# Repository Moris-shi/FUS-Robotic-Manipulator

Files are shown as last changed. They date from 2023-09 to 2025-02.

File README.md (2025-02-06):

# FUS-Robotic-Manipulator

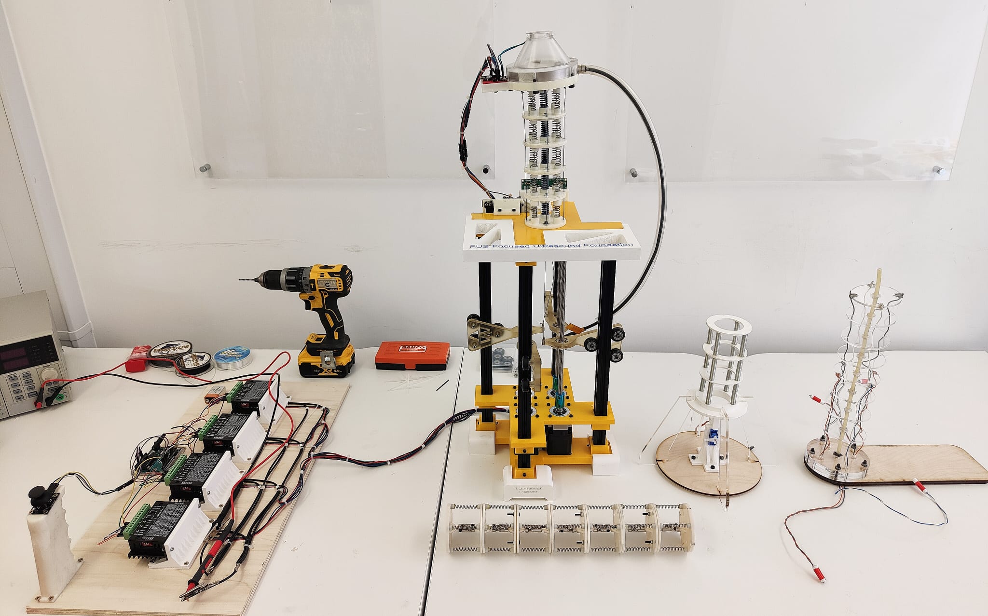
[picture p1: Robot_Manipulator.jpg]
image alt

 
Please refer to the project abstract and FUS report first which contains all information on development of the manipulator and assembly instructions

The robot CAD files section contains all the components in .stl format. This was 3D printed on a Ultimaker 2+ connect printer but any other 3D printer with a sufficent build volumn could be used. For 3D printing, import the .stl files into Ultimaker Cura available at https://ultimaker.com/software/ultimaker-cura/.
The following quantities of each file is needed:

•	1 x Base Mount

•	1 x Stepper Motor Mount

•	1 x Top Mount

•	4 x Slider

•	4 x Base Support Legs

•	1 x Sideways Support Mount

•	4 x Stepper Motor TB6600 Controller Mount

•	1 x LCD Mount

•	1 x Arduino Mount

•	1 x Joystick Mount

•	10 x Tendon Ligaments

•	1 x Ultrasonic Transducer Mount

The hardware section contains an Excel spreadsheet with all the hardware which needs to be purchased including prices (UK) and non-sponsored, sourcing links.

Robot Code section contains the required Arduino codes for the project

Any questions please contact me at zcemxsh@ucl.ac.uk

I would also love to hear if any replications or improvements have been made

Thank you for taking the time to check out this project

# Acknowledgement
We acknowledge the Focused Ultrasound Foundation for providing funding and supporting this project through the 2023 Global Internship Program.

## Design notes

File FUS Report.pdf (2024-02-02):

## Developing an affordable open-source robotic platform for precisely manipulating ultrasonic transducers for laboratory experimental FUS studies

Xingzao Shi, Student Member, University College London and Dr Seyyed Reza Haqshenas, Lecturer Of Therapeutic Ultrasonics, University College London

DECLARATION

“I, Xingzao Shi, confirm that the work presented in this report was my own. Where information has been derived from other sources, I confirm that this has been indicated in the report.”

## Abstract

This report will provide in-depth documentation on the development of a robotic platform designed to manipulate focused ultrasound (FUS) transducer for therapeutic applications. It will begin with an introduction to FUS technology, highlighting the challenges associated with its manipulation in laboratory settings.

Subsequently, design specifications aimed at addressing these challenges will be outlined. A comprehensive background research and literature review follows, with a focus on selecting the optimal robotic mechanism for the manipulator.

Moving forward, the development process of the robot was documented, including the various prototypes and designs, as well as the integration of electronics and sensors. Additionally, assembly blueprints and step-by-step instructions for building the robot from scratch will be provided. Testing will be conducted at each stage of development, with detailed documentation of the results obtained.

Finally, the report will conclude by discussing potential avenues for future improvements and provide a comprehensive list of references for further reading.

## Acknowledgement

I would like to extend special thanks to the Focused Ultrasound Foundation (FUS) who generously funded this project as part of the Charles Steger ACCESS FUS internship. Their support has been indispensable in bringing this project to life.

I would also like to thank all the researchers whose findings have been invaluable in the development of the robot as well as UCL Mechanical Engineering for providing the facilities and workshop.

Finally, I also want to express my deep appreciation to Dr Reza Haqshenas for his unwavering support and mentorship throughout the project.

## Table of Contents

## List of Figures

## List of Tables

Table 1: | 20
Table 2: | 25
Table 3: | 38
Table 4: | 38
Table 5: | 43
Table 6: | 66
Table 7: | 68

## A) Background

## I – Introduction

Focused Ultrasound (FUS) is an emerging medical technology that uses ultrasound waves to treat various medical conditions. FUS works on the principle of focusing ultrasound waves onto a specific target area in the body. This was done by using multiple ultrasonic transducers and firing them so that all the individual waves focus on one point through interference and superposition. At the focal point, the high energy frequencies can cause thermal ablation and heating destroying the cells in the local area or it can trigger cavitation, imploding the target zone. [1] The focused nature means that the effect was only localized at the focal region without affecting surrounding healthy tissue. FUS was usually implemented with MRI guidance to locate and assess the treatment at the target location. Currently, it is used as a non-invasive or minimally invasive technique for therapeutic purposes in different medical fields, including oncology, urology, and neurology.

- Oncology: FUS was commonly used in the treatment of various types of cancer, including prostate cancer and uterine fibroids. In prostate cancer treatment, FUS can be used to precisely target and thermally ablate cancerous tissue within the prostate gland while minimizing damage to nearby structures. It was considered a less invasive alternative to surgery or radiation therapy.
- Urology: FUS can also be used in urology to treat conditions like kidney stones. The high intensity of the focused ultrasound creates shockwaves and shatters the kidney stones.
- Neurology: Neurological disorders such as Parkinson’s and essential tremors can be treated with FUS where the region of the patient’s brain responsible for the condition can be targeted.
- Drug delivery: The challenge of precise drug delivery can be solved by FUS. The drug was injected intravenously into the patient in temperature-sensitive gel carriers. Then, FUS can be used to raise the temperature of the target location melting the carriers and releasing the drug at the target location.

Benefits of FUS include reduced risk of infection, minimal scarring, shorter recovery times, and potentially fewer side effects compared to traditional surgical procedures. However, the effectiveness of FUS can vary depending on the specific condition being treated, the size and location of the target tissue, and individual patient factors.

## B) Motivation

In therapeutic ultrasound, ultrasonic energy was focused on the target tissue to induce bioeffects. To treat the entire volume, the ultrasonic beam was steered either electronically, mechanically, or electromechanically (in hybrid equipment). Electrical steering utilises an array of multiple transducers firing out of phase to direct and move the focal point of the ultrasounds through interference. This was a very versatile but expensive option. On the other hand, mechanical steering can be carried out by utilising a robotic platform whereby the transducer was attached to a robot and the focal point moved by controlling the robot.

However, current robot platforms for ultrasonic transducer manipulation are heavily commercialised and very expensive. Often, complex proprietary software was used to control them, and it was very difficult to modify the design for bespoke applications. Solutions such as the MGIUS-R3 cost upwards of 100,000 pounds [2] and although being very capable, the price makes it out of reach for most researchers. This was a problem, and a cost-effective DIY robotic platform needs to be developed to allow more researchers to be able to precisely control the position and orientation of ultrasound transducers. The project will be open-sourced to allow other researchers to access the required designs for 3D printing and add improvements to the design.

The robot needs to be affordable yet reliable and capable. It must also be possible for a fellow researcher with basic mechatronics knowledge and experience to fabricate. The following design specifications are based on the general requirements of researchers in focused ultrasound.

- Cost – The cost of the robot was to be kept under five hundred pounds for all materials and parts.
- Simplicity of design and construction – All components should be easily sourced online, and all custom parts should be 3D printed with .stl files available for download. The assembly should be clear and easy to follow using nuts and bolts rather than welds or wood joining work.
- Load carrying capabilities – The robot should be able to successfully manipulate an ultrasonic transducer weighing up to five hundred grams.
- Workspace – The robot should have a field of reach of around 300mm from the base to the tip of the ultrasonic transducer.
- Ease of use – The robot needs to have an intuitive and simple form of control with a user-friendly display interface. The codes for this should be open-sourced for further development and improvements.
- Precision – The precision of the robot should be in the tolerance of millimetres in terms of positioning and sensing.
- Durability – The robot needs to be durable for repeated operation within its intended use.

## II – Manipulator Selection

## A) Robot Mechanisms

From the motivation and parameters, a design for a robotic manipulator for the ultrasonic transducer was required. Initially, to start the designing process, a class of manipulator mechanisms needs to be selected. For this purpose, thorough research into different types of manipulators was conducted.

### 1) Serial Manipulators

A serial robot consisting of a series of interconnected links joined by moving joints in a sequential chain-like structure. [3] Each joint can either be prismatic adding a linear motion variable, or revolute adding a new rotational axis and degree of freedom. Either allows motion between their adjacent links, enabling the robot to manipulate objects in its workspace. Serial robots have a rigid base and an end-effector, which is the part of the robot that interacts with the environment or performs specific tasks. In this case, the end effector would be the ultrasonic transducer.

Figure 1: Serial robot manipulator [4]

An example of a serial robot is an articulated robot commonly seen in industrial applications such as vehicle assembly lines. These robots often have multiple revolute joints and thus multiple degrees of freedom allowing them to achieve a wide range of motions such as reaching, picking, placing, and manipulating objects within their workspace.

Serial robots excel in precision, accuracy, and repeatability in performing tasks. They can be programmed to follow specific trajectories and manipulate objects with high dexterity. However, due to their sequential structure, they may have limitations in terms of speed and payload capacity as high moments and torques occur around the joints.

To achieve motion, an articulated robot can include either revolute, linear or spherical joints.

- A revolute joint moves around an axis achieving rotational motion. It provides a single degree of freedom, allowing rotation along one axis while constraining motion along the other axes.
- A linear or prismatic joint can move in a translational motion along a single axis this can be in the form of a sliding mechanism or piston actuating the joint making it longer or shorter.

- A spherical joint can move in multiple degrees of freedom around a single point. It was the combination of three revolute joints with an axis that intersects at a common point.

### 2) Parallel Manipulators

Figure 2: Mechanism types [5]

A parallel robot utilises multiple independent kinematic chains and links to connect the base of the robot to the end effector. [6] Each kinematic chain was independently actuated, allowing the robot to move the end effector in a coordinated manner. The design of a parallel robot allows for simultaneous control of multiple degrees of freedom from a single joint. An example of a parallel manipulator was a delta robot with three kinematic chains. This design provides excellent speed, accuracy, and agility, making delta robots well-suited for tasks that require rapid and precise positioning such as pick and place operations.

Figure 3: Parallel manipulator [7]

One characteristic feature of parallel robots is that they distribute the forces and loads among multiple limbs, allowing for better stability and load-carrying capacity. This attribute makes them suitable for applications that require high stiffness and heavy payload handling, such as flight simulators, machining, and heavy-duty industrial tasks. Parallel robots are also known for their exceptional accuracy, as their design reduces the effects of individual joint and link tolerances, resulting in precise and repeatable motion. They are often used in applications that demand high accuracy, such as surgical robots and 3D printing.

However, parallel robots can be more complex to design, and control compared to serial robots due to the interdependencies between the limbs and the need for coordinated motion. In addition, their workspace was also more limited compared to serial robots, as the range of motion was constrained by the mechanical structure. Furthermore, parallel manipulators are very sensitive to small errors in control signals or component defects as a small error was magnified by the mechanism having a large knock-on effect on the position of the end effector.

### 3) Hybrid Manipulators

A hybrid manipulator incorporates elements of both serial and parallel robots to combine their features and leverage their respective advantages and overcome limitations. [8] For example, a hybrid robot might use a serial robot arm for precise manipulation tasks and incorporate a parallel mechanism for increased stiffness and load-carrying capacity. This helps to improve their versatility, adaptability, and efficiency in performing complex tasks.

Figure 4: Hybrid manipulator [9]

An example of a hybrid manipulator was a serial-parallel robot. This type of hybrid robot has a serial robotic arm for reaching long distances and performing complex tasks, along with a parallel mechanism before the end effector for increased stability, load-carrying capacity, or high-speed operations. The combination of serial and parallel components allows for improved performance in terms of precision, speed, and versatility.

However, hybrid manipulators are the most complex to design, code and manufacture. And their nature of combining serial and parallel components makes them the most expensive option. Furthermore, hybrid mechanisms have increased failure points which make them less reliable and require more maintenance.

### 4) Cartesian Manipulators

Cartesian manipulators are very simple in design and can have a very large workspace. As a result, they are primarily used for transferring heavy objects from one place to another. [10] The gantries are mutually perpendicular to each other and mobilised using stepper motors and belts for precision control. This was the cheapest method to manipulate objects including pick and place operations and CNC (Computer Numerical Control) machine tooling.

Figure 5: Cartesian manipulator [11]

Cartesian robots are known for their higher payload-carrying potential, cost-efficiency and ease of programming. Additional modules can also be added to the already existing mechanism to increase the motion capabilities of the robot. More advantages of this robot category are that it showcases higher skill in precision and accuracy, plus it consumes smaller factory space to operate compared to other robotic counterparts.

Despite their advantages, Cartesian robots may have limitations in terms of flexibility and manoeuvrability compared to robots with articulated or parallel kinematics. The linear motion along orthogonal axes may not be optimal for tasks that require complex or curved trajectories.

### 5) Tendon-driven Manipulators

Tendon-driven robots or continuum robots a robotic mechanism inspired by flexible and continuous structures found in natural organisms like octopuses and elephant trunks. They are designed to mimic their flexibility, dexterity, and adaptability, making them well-suited for tasks that require navigating through complex and constrained environments. [12] Continuum robots are often composed of soft materials or have flexible segments allowing them to bend and twist. This flexibility allows for a wide range of motion and helps robots reach spaces that might be inaccessible to traditional rigid robots. These traits make tendon-driven robots ideal for applications such as minimally invasive surgeries and search and rescue operations.

The continuous and soft nature of continuum robots presents both challenges and advantages. They are generally more adaptable to different environments but may require advanced control algorithms to accurately manipulate them.

## B) Selection Process

Figure 6: Continuum robot [13]

Out of the five mechanisms, one needs to be chosen for implementation. This was done with careful consideration of the design specifications.

The simplicity of design and construction was of utmost importance for others without a manufacturing background to replicate. As a result, the mechanism needs to be simple preferably using as few moving parts as possible. The optimal candidates for this would be cartesian robots with three axes of motion needed for the gantry or continuum robot with its driving motors only responsible for pulling on strings to actuate a tendon. The complexity and high number of parts required for parallel and hybrid robots are unsuitable for this factor. Serial robots can also be considered as a potential candidate although being more intricate than the others.

The workspace and capability of the design also need to be considered. In ultrasonic transducer manipulation, it was crucial to be able to control the orientation of the transducer. This eliminates purely cartesian systems because only the position of the transducer can be controlled and not the orientation. As a result, the mechanism was unsuitable for applications where the sides of subjects need to be treated by FUS.

Thus, serial and/ or continuum robots are both well suited for this project where simplicity of design and capability are dictating factors. Both are equally viable for the required applications and have a similar range of workspace. However, since continuum robots are still under development, further research into the field can be beneficial not only for FUS research but also towards the advancement of continuum robotics in general. Therefore, continuum robots are chosen as the mechanism for manipulating FUS transducers.

## C) Terminology

- Degrees of freedom – A degree of freedom refers to the ability of motion for a robot. this can be translational in the x-y-z axis or rotational about an axis. Each degree of motion removes a motion constraint and a robot with six degrees of freedom can move to any position and orientation in 3D space.
- End effector – The end effector sits at the end of the robot and is the component responsible for interacting with the task. For example, the bucket was the end effector of an excavator machine.
- Robot workspace – The workspace of a robot defines the region around the robot that the end effector can potentially reach. A robot’s workspace was dependent on its link lengths and joint configurations.
- Robot links and joints – Robot links are the rigid members connecting the joints. They are solid components with no motion capabilities. The joints are the movable components of the robot that cause relative motion between adjacent links.

Figure 7: Serial robot features [14]

## D) Literature Review On Continuum Robots

Currently, continuum robots are still in their infancy stage with incomplete mathematical modelling and developing prototypes. The aim was to develop a controllable mechanism to have the properties of that of continuous, soft organisms such as octopuses. This was different from that of traditional robots which use rigid joints without flexibility. Continuum robots are controlled by actuators which can be positioned away from the mechanism rather than being on the mechanism as joints. Currently, as of August 2023, there have been numerous studies and experiments carried out to explore the discipline.

### 1) COAST

The coaxially aligned steerable (COAST) guidewire robot was developed by the Georgia Institute of Technology in 2021. [15] It was developed as a manipulable catheter for performing cardiovascular surgeries in arteries as manual guidance was the only solution at the time. This was a slow and risky process where the surgeon required extensive skill and experience to navigate the catheter to the target zone using fluoroscopic images. This exposed the surgeon to high levels of radiation making the practice unsustainable.

The COAST robot uses a flexible, nitinol inner and outer tube which can be independently actuated. The inner tube was connected to the outer tube via a joining insert at one end. Actuating the inner tube relative to the other tube thus causes a change in the trajectory of the catheter. The tendon was also fitted with pressure sensors so that the surgeon could determine whether excessive force was being applied to the walls of the arteries.

Figure 8: COAST manipulator

An algorithm was also developed to calculate the trajectory which the robot needed to take from entry to the target zone using images from fluoroscopic images. This was successfully done with the hardware having a reported mean error of 2.87 mm deviation from the computed path.

### 2) REDSLAB

Figure 9: COAST manipulator

The Imperial College London REDSLAB developed an open-source continuum manipulator for surgical robotics research. [16] The tendon was a flexible 3D-printed TPU rod actuated by strings. The robot was actuated by four strings which are controlled by a servo pulley mechanism such that rotating the servo arm causes the pulley to also rotate. This pulls on the string in one direction while giving slack to the string directly opposite allowing the robot to bend mimicking that of antagonistic pairs in muscles.

Figure 10,11: Antagonistic continuum robot

Three sections were made each actuated by 2 sets of pulleys giving the robot 6 degrees of freedom using 6 servo mechanisms. It was also possible to see that the first joint located closest to the base has 3 wires passing through to independently control the next 2 sections.

Figure 12: Flexible tendon

The entire robot was controlled by an Arduino UNO which can be programmed to follow a path and has a good field of workspace around the tendon to position the end effector.

Figure 13: Robot workspace

## III – Iterative Design Process

## A) Prototype One

### 1) Prototype Aim

The first prototype aims to evaluate the feasibility of a tendon-driven robot and to create a physical model to inspire new possible designs. The prototype acts as a base for the other iterations to improve upon. As a result, it needs to demonstrate all the basic mechanisms for a tendon-driven device and be quick and simple to fabricate at a low cost. For this purpose, a segmented, sting-pulled tendon was proposed. The prototype will have a flexible, incompressible backbone to support and hold each one of the ligaments. The ligaments themselves need to allow the strings to pass through and have a method of being attached to the backbone. In terms of degrees of freedom, four DoFs were chosen allowing the tendon to be driven in any direction on two joints.

### 2) A Note On Nuts And Bolts

In the following sections, many components are designed to be fixed with nuts and bolts. Everything in the build was designed to be secured using M3 bolts meaning a bolt with a 3mm diameter shaft. This kit from Amazon will include all the fixings necessary for the build (link in the cost of robot section of the report).

Figure 14: Nuts and bolts [17]

However, the instructions will not include the length of the bolts. This was because the length of bolts only needed to be long enough to pass through the subjects and leave room at the end for a nut. As a result, the exact lengths of the bolts aren’t very important as long as they can pass through and secure the robot.

### 3) CAD Model

The following design was developed in Fusion 360 [18] whereby the tendon can be manipulated by two sets of four strings on eight ligaments. The strings extend out of the case of the device and are actuated by hand pulling on individual springs. One set of the four strings will pass through the base onto the fourth ligament whereas another set will pass on the inner pass from the base to the furthest ligament. This gives a joint at the base and another one at the fourth ligament achieving the four degrees of freedom. A rubber tube was chosen as the central backbone as a spare part lying around the workshop. Alternatively, any semirigid PVC tubing or even hot glue rods can also be used to achieve the same effect. The ligaments are made of laser-cut acrylic and have an outer diameter of 700mm allowing for easier manipulation as the further away from the centre the strings are attached, the more precise the tendon becomes. Individual ligaments are spaced 35mm apart to achieve an overall reach of 320mm which meets the requirements in the brief. A base ligament was also introduced to allow the rest of the tendon to be fastened to the base.

Figure 15: CAD model of prototype one

### 4) Manufacture And Assembly

The base was laser cut out of wood and 2 sets were made to increase the strength of the base adding to 10mm. The ligaments are also manufactured from 5mm thickness acrylic.

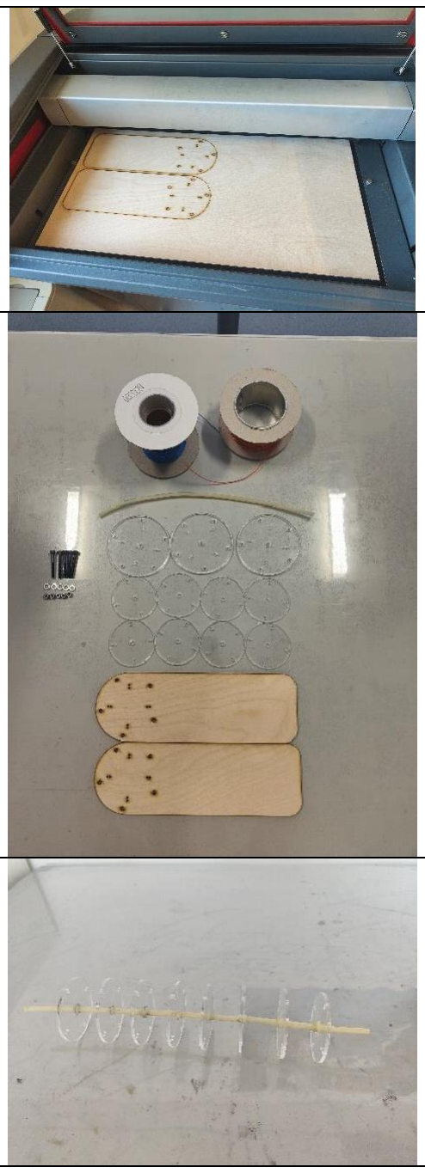
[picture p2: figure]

All the parts required for the prototype are shown here including five M3 X 45 bolts and accompanying nuts and washers. For the strings, electrical wires were used as it was the only available option at the time but a braided fishing line would be ideal for the purpose.

The tendon was assembled by gluing the ligaments at set distances marked 35mm apart using a hot glue gun. A 45mm gap was left at one end to accommodate the thickness of the wooden base.

The wires were connected to the tendons with one set of four attaching to the fourth ligament and another passing within the inner drill-outs to the end ligament. The wires were then tied and securely fastened with a reasonable length protruding out of the base allowing the tendon to be pulled and driven by hand.

The base was assembled by bolting the wooden base and acrylic tendon base together with nuts and bolts.

Finally, the base was hot glued to the tendon with the wires passing through and the prototype was complete.

Table 1: Manufacture and assembly of prototype one

### 5) Testing

For testing purposes, the base was fastened to a table with a clamp so that the strings could be manipulated. By pulling on the outer wire connected to the end of the ligament, the tendon can be made to go in that chosen direction curling up. By pulling on its adjacent wire, the tendon can be manipulated to move towards the latter direction depending on the applied force.

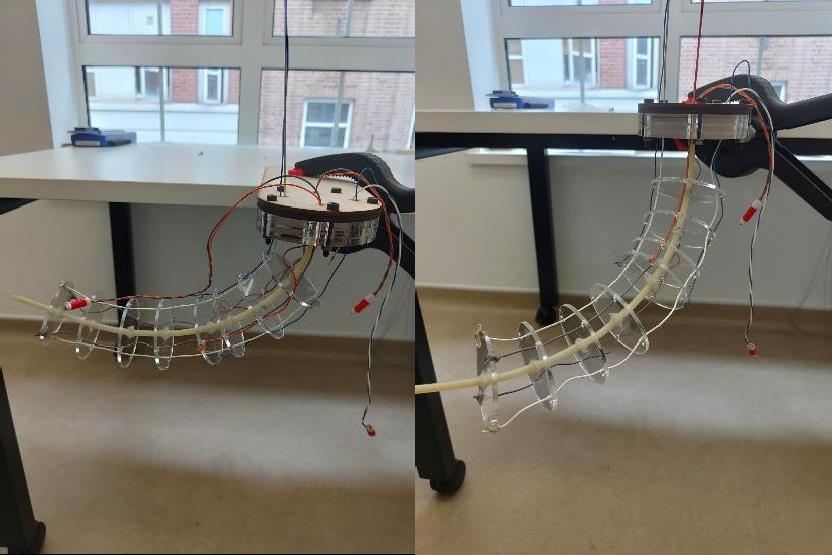
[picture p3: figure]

Figure 16,17: Tendon manipulation with end string

A similar effect can be seen when the inner wire was pulled, although this only affects the first four ligaments and does not impact the end four ligaments.

Figure 18: Tendon manipulation with inner string

When both the inner and outer wires are pulled simultaneously, the tendon can be manipulated in much more interesting ways, for example. Pulling on the same side makes no difference whereas opposing sides cause the tendon to bend back on itself. Finally, pulling adjacent wires results in a twisting motion in the joint.

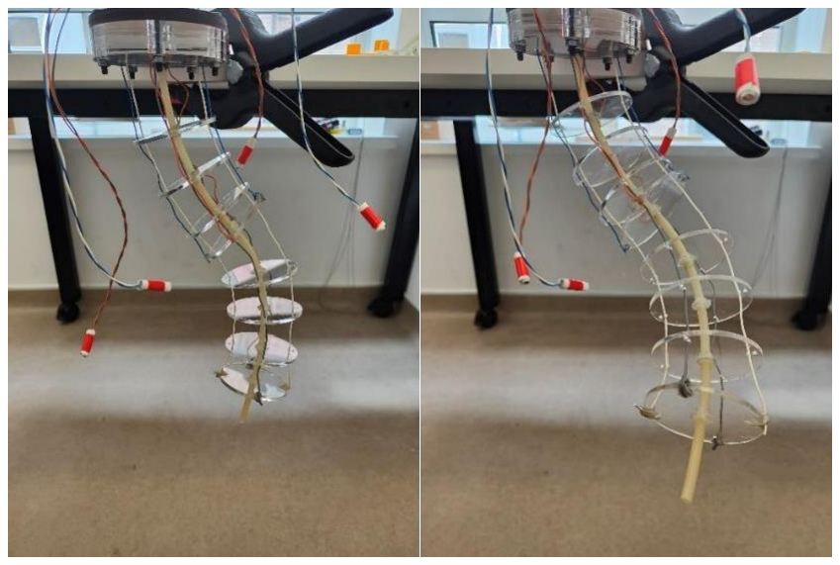
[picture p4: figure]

Figure 19,20: Tendon Manipulation with multiple strings

Many more combinations are possible to manipulate the tendon’s shape and orientation.

### 6) Prototype Evaluation

The prototype can be deemed a success in demonstrating the feasibility of a tendon-driven robot. It successfully shows that the position of the end effector can be manipulated and placed within space by individually actuating each of the strings. However, the tendon was very unstable in the upright position and tends to collapse so it could only be reliably used in the upside-down orientation. Furthermore, the backbone was not strong enough to support the robot in a sideways setup. Finally, as a first prototype, there was no way of controlling the tendon electronically and everything was done manually which was unintuitive and difficult.

## B) Prototype Two

### 1) Prototype Aim

The second prototype aims to motorise the tendon as well as making it much stronger to be used in the upright and sideways orientation. For this purpose, an Arduino was introduced to act as the control interface for the robot. To keep the cost down, only two degrees of freedom are designed so only a single set of four strings needs to be actuated and this can be easily scaled up if the prototype proves successful. The Arduino will control two sets of servo motors since only one of the strings in an axis was pulled at any time to achieve motion so by connecting two strings to one servo, the full range of motion can be achieved.

Figure 21: SG-90 micro-stepper [19]

To strengthen the tendon, a new mechanism was proposed to use springs for the backbone. This was because springs offer a resistance to motion which would help the tendon to stay in its original position no matter the orientation as well as when a load such as the ultrasonic transducer was applied. This was at the expense of the tendon requiring higher actuation forces since now the servo will also have to overcome the resistance of the springs.

### 2) CAD Model

Figure 22: CAD model of prototype two

The above model was designed for the second prototype. The new tendons are reinforced with four springs between each ligament positioned equidistant from the string pass-throughs. Three sets of springs are used with four ligaments spaced 40mm apart to achieve a total workspace of 160mm. The springs have an inner diameter of 5mm so four circular extrusions protruding 5mm out of each ligament were modelled to indicate where the springs need to be placed in assembly as well as reinforcing the joint by adding more surface area for the gluing process. The base ligament also includes attachment points to allow it to join the base section. A two-part design was utilised to allow the tendon to be swappable with other, future designs.

Figure 23: Ligament CAD

The base section comprises of a stand to mount the two stepper motors as well as attachment holes to bolt it to a wooden base. The housing positions the steppers in such a way that the servos’ adapters are parallel and directly underneath the exit for the string of the tendon. To join the sections together, four acrylic fins were used to connect the base of the robot to the top allowing the robot to be in an upright position.

### 3) Manufacture And Assembly

All the required components were 3D printed on the Ultimaker 2+ connect printer but any printer with a sufficient bed size could also be used. Cheaper alternatives like the Ender 3 series are a great more cost-effective solution. The material used was white PLA which was standard with all 3D printers. The acrylic supports and the wooden base was also laser cut out of 5mm sheets.

All the required parts for the build are gathered including four M3 X 12 bolts and M3 nuts, twelve 7mm by 42mm springs and an Arduino with two stepper motors and jumper cables. The microcontroller was an Arduino UNO which has more than sufficient ports for the project and the SG-90 micro-stepper motor was chosen as it came with the kit purchased (link below in cost section). The servo’s orientation can be controlled by manually rotating a potentiometer.

The springs were glued onto the ligaments using epoxy resin or Araldite for increased strength and durability to hot glue since the forces in the joints are much stronger in this prototype.

The servo housing was fastened onto the base plate with nuts and bolts and servos were inserted. Here, only one servo was present to test if the design works.

The acrylic support fins are attached to connect the robot base to the tendons.

Strings are strung from either end of the servo to the end of the tendon and tied at ends once in tension.

The Arduino circuit was wired in the following manner and the system was programmed in the Arduino IDE program completing the build (code can be found in Appendix 1).

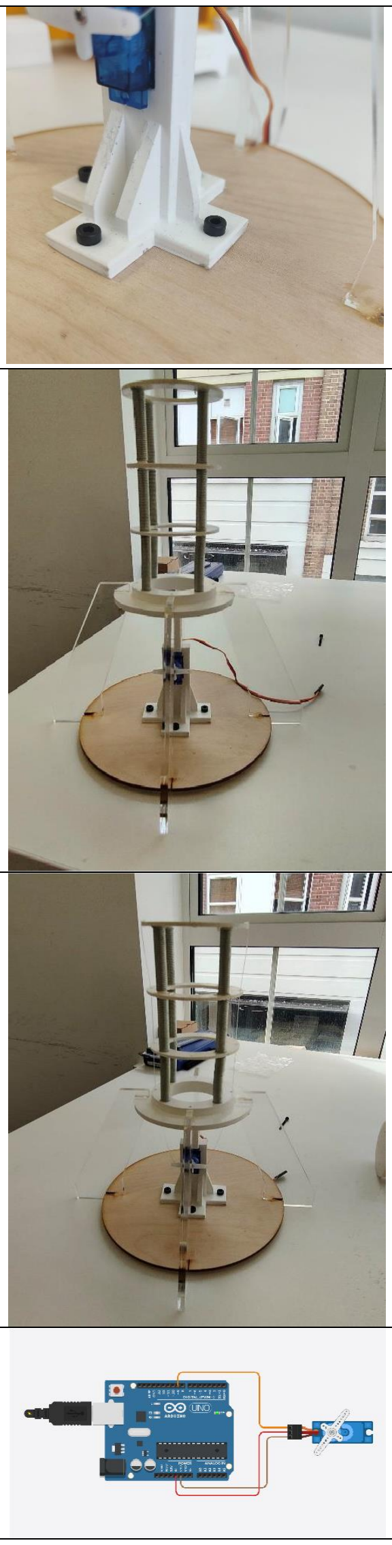
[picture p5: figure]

Table 2: Manufacture and assembly of prototype two

### 4) Testing

Upon testing, the stepper motors did not generate enough torque to pull the strings and manipulate the robot. Thus, an attempt was made to manually drive the tendon by hand pulling on the strings.

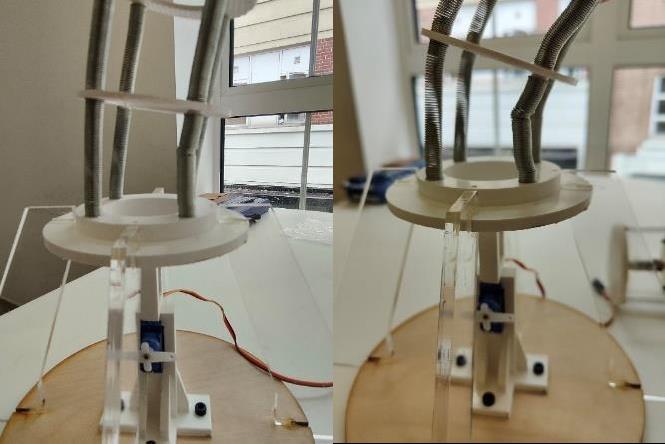
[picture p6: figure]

Figure 24,25: Collapse of tendon spring joints

Here, the tendon was very difficult to manipulate, and a very large amount of force was required to move it. Then once the tendon starts actuating, two sets of springs very quickly undergone collapse rendering the mechanism unsuitable for use. The cause for this was due to the springs being extension springs which meant it was not possible to become compressed making it act like a rigid joint under compression. As a result, a large force was needed to overcome this leading to collapse. Due to this, the second servo motor was not connected to the robot. Furthermore, it was noticed that since the strings were attached at an angle to the base, abrasion would cause an issue as the string was dragged along the edges of the base.

Figure 26: Strings attached at angle causing abrasion

### 5) Prototype Evaluation

The prototype was not successful in achieving electronically controlled manipulation of the tendon but it did provide a lot of insight for future iterations. Features which should be kept include the two-part design for the tendon and driving mechanism allowing for modulization and testing different designs without redesigning the others saving time and cost. A stronger drive mechanism was required and should pull the strings directly underneath and not at an angle to prevent abrasion to the strings increasing the design’s lifespan. In terms of tendon design, springs offer a solution to the issue of the tendon collapsing under load but these need to be changed to compression springs to allow the spring to both expand and contract.

## C) Prototype Three

### 1) Prototype Aim

For the third prototype, a two-part design system was implemented with separate prototypes for both the driving mechanism and the tendon. This allows for the optimisation of both systems without having an impact on each other. Sensors were also implemented to provide the user with essential information about the transducer.

### 2) Sensors

To fully and safely utilise the ultrasonic transducer, certain variables such as orientation and distance between the transducer and subject need to be identified. Orientation was important as the transducer needed to adapt to the curvature of the animal and thus it was important to know the orientation of the ultrasonic transducer. A distance sensor was needed to identify the distance between the transducer and the subject. A method of telling whether the transducer was in contact with the subject was also crucial as the cone needs to be directly in contact with the subject with no air gaps for the ultrasound to fully propagate.

2.1) Orientation
The orientation of the transducer within 3D space can be determined with a gyroscope. Digital gyroscopes measure angular velocity and acceleration and then through processing, the raw values can be computed to become orientational tilt in the X, Y and Z axis. The chosen gyroscope was an MPU 6050 which was a three-axis gyroscope capable of measuring tilt and acceleration in all three axes.

Figure 27: MPU6050 gyroscope [20]

It was also fully compatible with Arduino and cheap costing around three pounds per unit. The circuit plugs need to be soldered onto the sensor and the rest of the circuit was wired as follows:

Figure 28: Arduino wiring diagram for MPU6050 [21]

2.2) Distance
The distance sensor must have a high resolution so the user can get a precise understanding of the distance between the target and the transducer to not crash it into the subject harming it. The latency of the sensor must also be very quick to assess the instantaneous distance without a time delay. It must also be small and light enough to fit onto the robot without weighing it down. Two separate, similarly priced, sensors were considered including an ultrasonic and infrared sensor.
- Ultrasonic sensor – The HC-SR04 was a very common distance sensor which uses a sender and receiver to determine the time delay between the sent and received ultrasound signal and thus calculate the object's range based on the speed of sound through air. It has a maximum range of 400cm and a minimum range of 2cm with a resolution of 1 cm. [22]

Figure 29: HC-SR04 ultrasound distance sensor [23]

- Infrared sensor – The VL53L0X was a time-of-flight sensor which measures distance based on the speed of infrared radiation. It contains a module which sends pulses of infrared light and a receiver detecting and determining the time taken for the pulse to be reflected. It has a range of two meters and no blind distance like the ultrasonic sensor. It also has a higher resolution of 1mm. [24]

Figure 30: VL53L0X infrared distance sensor [25]

From the comparison, the VL53l0x was chosen as the distance sensor since it has the higher resolution of 1mm which gives the user a much greater level of accuracy regarding the distance to the subject. It was also smaller and lighter making it perfect for the project. The pins are once again soldered on and the rest of the circuit was wired as follows:

Figure 31: Arduino wiring diagram for VL53L0X [26]

2.3) Pressure
The pressure exerted can be determined by a force-sensitive resistor, the sensor uses piezo electrics which change resistance based on how much force was applied to it.

Figure 32: Pressure contact sensor [27]

Then a voltage divider circuit can be set up with an Arduino to convert the resistance to voltage and the force can be calculated based on the properties of the sensor given by the manufacturer. It was very light and small making it ideal for the application. The wiring for the circuit was as follows using a 10kOhm resistor:

Figure 33: Arduino wiring for pressure contact sensor [28]

2.4) Display
To present all the information to the user, a compact LCD screen was used. The LCD chosen was a standard 16-pin interface which displays data controlled by an Arduino. The LCD was wired as follows with a potentiometer and 10kohm resistor:

Figure 34: Arduino wiring diagram for 16x2 LCD display [29]

From this, the X and Y-axis tilt, distance and pressure are displayed on the LCD. The Z-axis data was not displayed as the tendon does not twist so it was constant.

2.5) Assembly
The wiring for all three sensors and LCD was connected to an Arduino Uno using the circuits provided. Since three 5V and ground supplies are needed but only one port was provided on the Arduino, the 5V supply and ground are connected in parallel to all three sensors on a breadboard shown below. The LCD was connected to the 3.3-volt outlet. The code for all the sensors and LCDs can be found in Appendix 2.

### 3) Driving Mechanism

Initially, a stronger servo was considered to replace the weaker servos. These would be in the same orientation as prototype two but have longer, custom-made arms to reach under the tendon string attachment points. However, it became evident that the arms would be subjected to very high loads and would most likely require to be machined out of metal putting it out of budget and accessibility for the project. In addition, all the forces are concentrated in the servo motor which can cause long-term damage and overheating issues. Furthermore, the nature of the design means that as the arm was rotated to pull the strings, it would trace an arc which would wear out the string and exert less force requiring further correction. All these factors ultimately lead to the rejection of this mechanism.

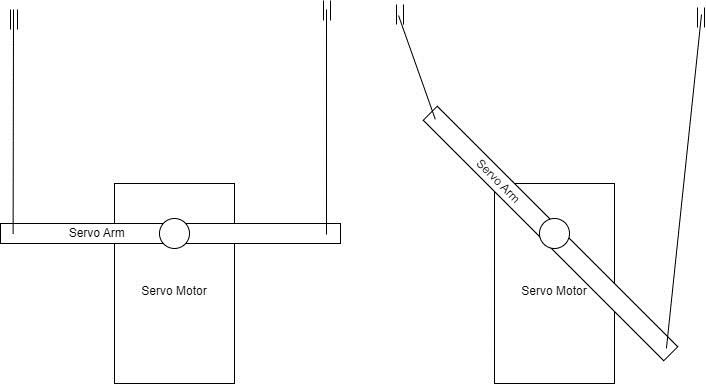
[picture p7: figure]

Figure 35: diagram showcasing the drawbacks of using servo motors and arms

The next design came from a cartesian rail system found in 3D printers and CNC machines. The mechanism uses stepper motors connected to a threaded rod via a coupling. A slider with a screw adaptor was then fitted onto the threaded rod and fitted to a sliding rail with bearings. As the motor spins, the rod connected by the coupler also spins. The screw adaptor acts to translate the rotational motion into linear motion which moves the slider up and down the rail.

Figure 36,37,38: Cartesian rail system found on 3D printers

This was ideal for the design as it allowed for much more precision and control. The screw adaptor also acts to magnify the rotational force generated by the stepper motor to the linear force meaning more force can be exerted to pull the tendons. As a result, stronger springs and longer tendons can be incorporated whilst withstanding the weight of the transducer. The nature of the mechanism allows it to be placed directly under the tendon and always pull the strings vertically down eliminating wear through abrasion. Moreover, all the forces are also offloaded onto the slider instead of the stepper which means that the position was held so that the motor was not subjected to the resistance of the compression springs prolonging lifespan and reducing the risk of overheating leading to longer operation times during use. These factors are very promising, and a new design was made based on this mechanism. Four stepper motors were proposed each with the sliders having an attachment point to pull the strings. The stepper motors will be controlled by an Arduino microcontroller with an intuitive user input.

3.1) CAD Model

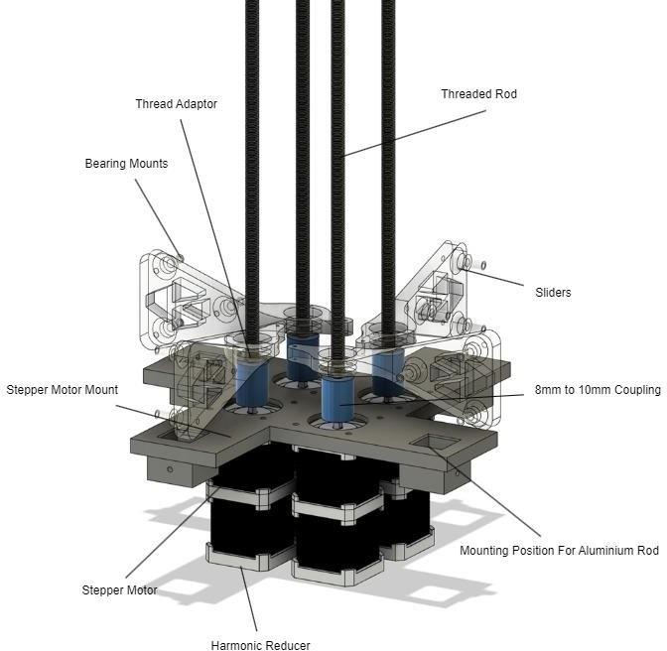
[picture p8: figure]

Figure 39: Initial CAD model of driving mechanism

The stepper motors chosen were NEMA 17 motors with a torque of 0.55 Nm. In addition, each stepper was paired with a harmonic reducer. The harmonic reducer is a gearbox which reduces the input speed but increases the output torque. Reducers are commonly used in industrial robots to achieve the high torques required for each joint. Likewise, in the case of the robot, torque takes priority before speed to generate enough force to pull the strings. The reducers chosen have a gear reduction of five times so it can amplify the torque produced by the motor to 2.75 Nm.

Figure 40: NEMA 17 stepper motor and reducer pair

In this design, four of the stepper-reducer motors were utilised giving three degrees of freedom. Each can independently drive a threaded rod via a coupling. The diameter of the threaded rod was 6mm whereas the output shaft diameter of the reducer was 8mm so a 6mm to 8mm adapter was used. To fix the drivers in place, the amount was designed to be bolted into the pre-existing mounting fixtures on the harmonic reducer. The mount also has cutouts to allow a 20mm by 20mm aluminium extrusion to be inserted as the structure support chassis. To convert the rotational movement to linear actuation, a slider was designed to house the threaded adaptor secured by M3 bolts. The slider also has a fixture for the line to actuate the tendons as well as three mounts for bearings which are designed to tightly fit into the grooves of the aluminium extrusion.

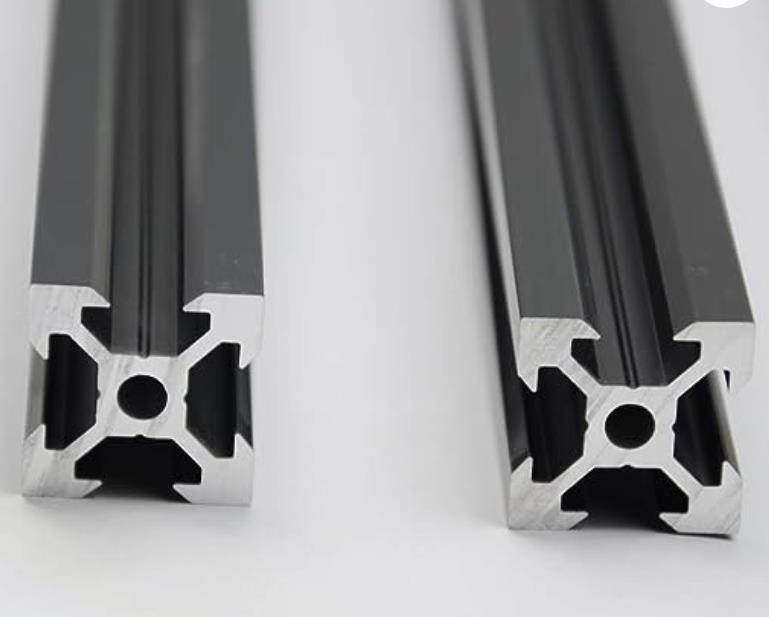
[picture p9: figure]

Figure 41: 2020 Aluminium extrusion [30]

3.2) Stress testing
The sliders are responsible for pulling the strings and are thus subjected to high amounts of force and pressure. To ensure the component will hold up to the forces and not fail under load, stress element analysis was carried out in Fusion 360. The model was fixed in the screw mount holes for the thread adaptor since this will be fixed to the threaded rod on the actual build.

Figure 42,43: Constraints and forces applied in simulation

Then the material (3D printed ABS) was applied to the subject and a force of one hundred Newtons pulling up on the string mount was applied. One hundred Newtons were chosen as a baseline force to determine the maximum load the component could withstand before collapse.

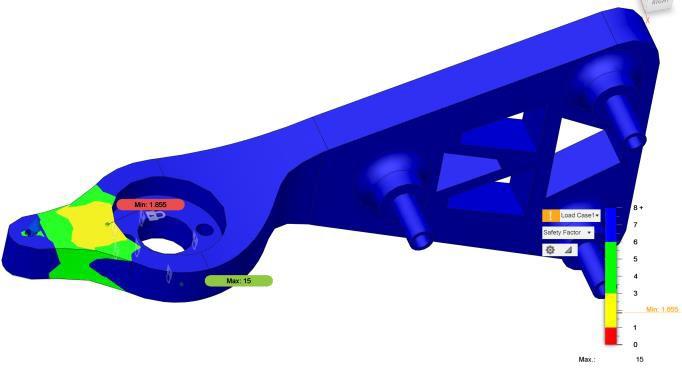
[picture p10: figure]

Figure 44: Safety factor simulation results

The simulation was carried out and a minimum safety factor of 1.855 was identified. This means that the slider will fail when a load of 185.5 Newtons or 18.86 Kg was applied.

Figure 45: CAD model with base mount on the right

Following this, a base mount was added to secure the aluminium extrusion as well as to stabilise the drivers. Routing cutouts were also included to help manage the stepper motor wires. The CAD was updated with the bearings thread adaptor in place as well as the bolts needed to secure the mounts to the aluminium chassis. Additionally, a top mount was added to secure the threaded rods and prevent vibrations during operation. Bearings were chosen for this purpose with the added benefit of reducing friction. Furthermore, it serves as the interphase between the driver unit and the tendon joints with M3 mounting holes on top and cutouts vertically above the sliders to allow the line to pass through.

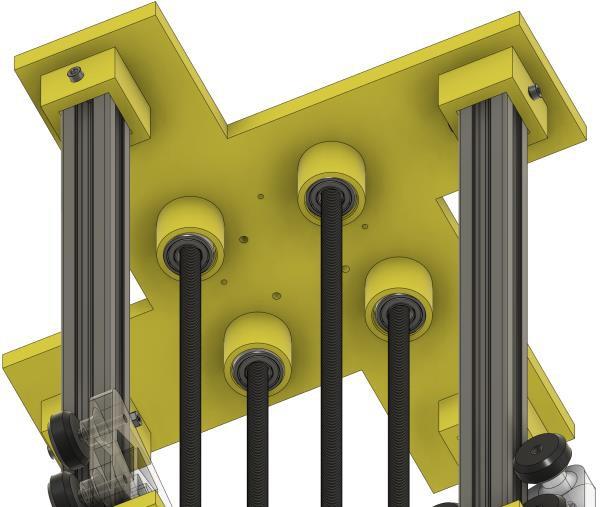
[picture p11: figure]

3.3) Electronics

Figure 46: CAD model of top mount

Each of the stepper motors requires much higher voltage and current than an Arduino can output so a separate power source was required. However, this results in no way to control the steppers thus a motor driver module was needed to relay the Arduino code and amplify the signal’s voltage and current. A TB6600 was chosen as it offers the necessary performance and cooling required at a low cost.

Figure 47: TB6600 stepper motor driver [31]

The wiring diagram from the Arduino to the TB6600 to the stepper motor is shown below. Each of the ports on the driver can be loosened by a precision screwdriver and then retightened once the wire was inserted.

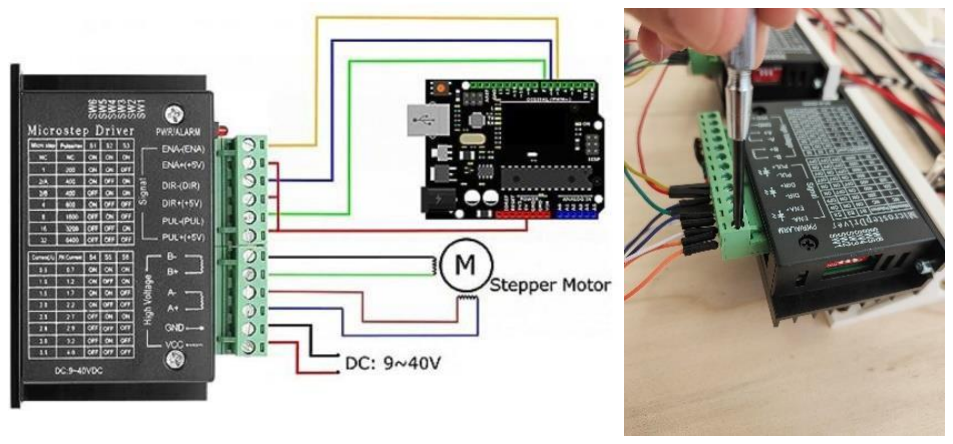
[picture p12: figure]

Figure 48: Arduino wiring diagram for TB6600 [32]

The setting for the driver needs to be set to the following preset with switches 2,3,4 flipped on so that they are pointing downwards:

Figure 49: Setting switch position configuration

The ground and VCC pins need to be wired to a power supply capable of generating at least 9V whereas the rest of the pins in the high-voltage section were connected to the stepper motor. Within the signals section, the DIR pin dictates the direction of the motor spin (clockwise for a positive voltage from the Arduino and anticlockwise for a negative signal). The PUL pin detects the pulse width from the Arduino and converts it to the rate of motor rotation based on the average voltage. Thus, a high average voltage with less delay between each pulse width will result in a greater rate of rotation than a low average voltage with more delay between each pulse.

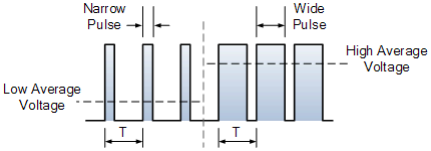
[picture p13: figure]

Figure 50: How a stepper motor is controlled by PWM [33]

The enable pin acts as a switch to turn the motor on or off. However, the motor driver was on in its default setting so to save space on the limited Arduino UNO ports, the yellow wire was also connected to ground.

Figure 51: Stepper and controller testing

During this time, an alternative driver was also tested, being the Arduino CNC shield. The module was very compact and plugged directly into an Arduino for a much smaller form factor. The shield can control four motors at once with four built-in mini-stepper controls. However, many failed attempts were made to operate this driver with issues such as overheating and code bugs, so this was eventually discarded to allocate time to other developments.

Figure 52: Arduino CNC shield driver

With a successful trial of the TB6600 stepper driver, three more units were made to drive each of the four steppers independently. The DIR and PUL pins are assigned and connected to the Arduino in the following fashion:

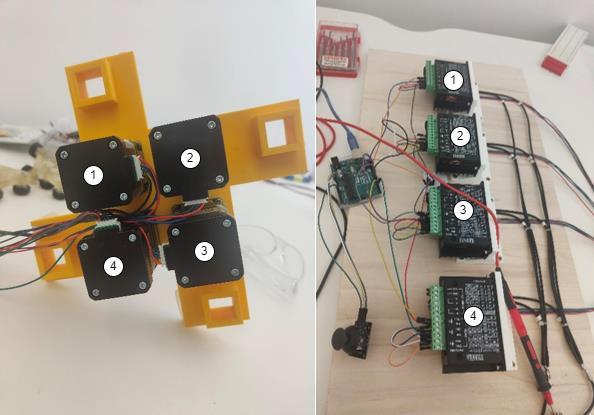
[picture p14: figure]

Figure 53,54: Stepper to controller mapping

Stepper motor number | Dir pin on Arduino UNO | PUL pin on Arduino UNO
1 | 3 | 2
2 | 5 | 4
3 | 7 | 6
4 | 13 | 12

Table 3: Individual stepper pin assignments to Arduino UNO

Both four VCC voltage and ground cables were spliced and soldered into one wire to allow the entire system to be powered by one power supply. Furthermore, an interface to control the robot was used in the form of a joystick since it was very intuitive and familiar to use. In this case, the SW pin on the right-hand side which detects If the button has been pressed down was not used. All the codes for the driver section of the robot can be found in Appendix 3.

Figure 55: Arduino wiring diagram for joystick [35]

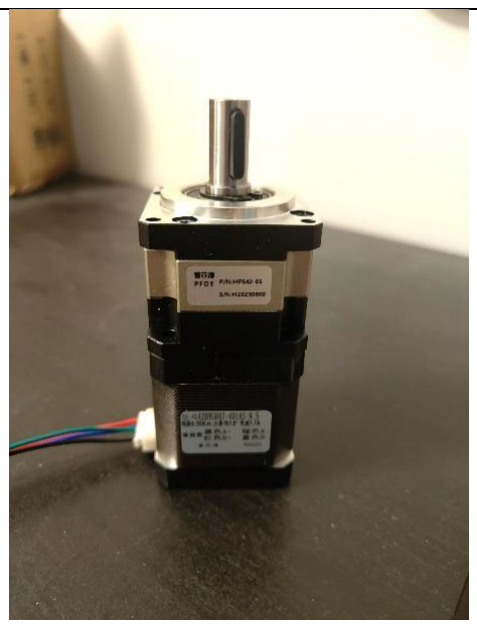
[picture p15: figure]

3.4) Manufacture And Assembly The stepper motor and harmonic reducer were bolted together with the included hardware.

The stepper motor controllers and joystick were wired and installed onto a wooden board with the 3D printed controller mounts.

The base mount was fabricated and the stepper motor wires were passed through the centre for convenience.

The stepper motor mount was 3D printed and the motors were secured by M3 bolts and nuts. Take note to orientate the motors in this fashion.

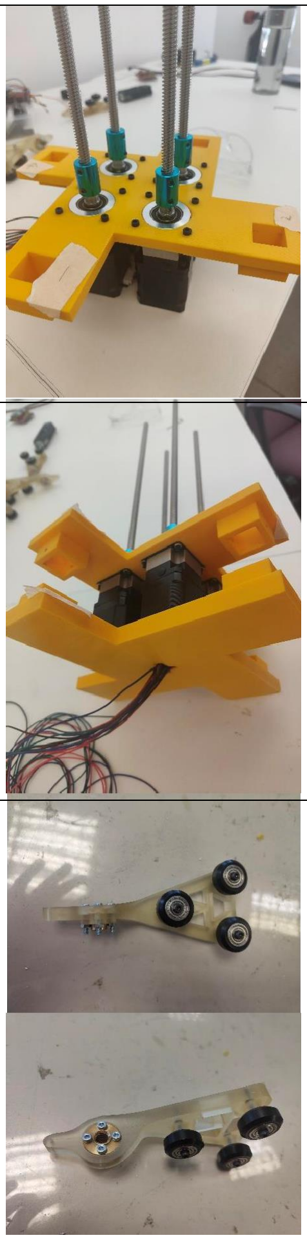
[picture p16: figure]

The coupling and threaded rod were installed onto each reducer and tightened with an Allen hex key.

The base mount was attached and secured via a friction fit.

The sliders were 3D printed via a Harlot Lite Resin 3D printer which offers superior quality and detail to standard extrusion printers. The bearings and thread adaptor were then fitted with M3 bolts and nuts.

The aluminium extrusions were cut to length of 400mm by hacksaw. 3mm holes were then drilled in the centre along intervals of 13mm, 78mm and 387mm from one end. This was done on a pillar drill but was also possible with a hand-held cordless drill.

The prepared aluminium chassis was inserted into the 3D printed mounts noting the mounting position for M3 bolts.

The four sliders are slotted into the rails and threaded on by hand rotating the coupling anticlockwise until all 4 reach the middle position along the threaded rod.

The top mount was 3D printed and the bearings press fitted or with Araldite into the housing. It was then inserted into the main frame.

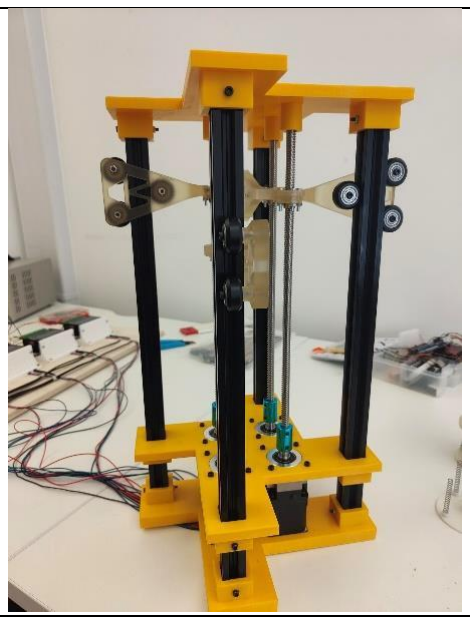
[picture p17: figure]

Twelve M3 bolts were added to secure the top, middle and bottom mount to the aluminium extrusion via the pre-drilled holes.

Four support feet and a holder was also designed and 3D printed so that the prototype can also be oriented in a landscape position on its side.

To secure the Arduino UNO and LCD to the robot, mounts were designed and fabricated to be attached with M3 bolts.

The robot was powered by connecting to a power supply set to 18 Volts and 5 Amps.

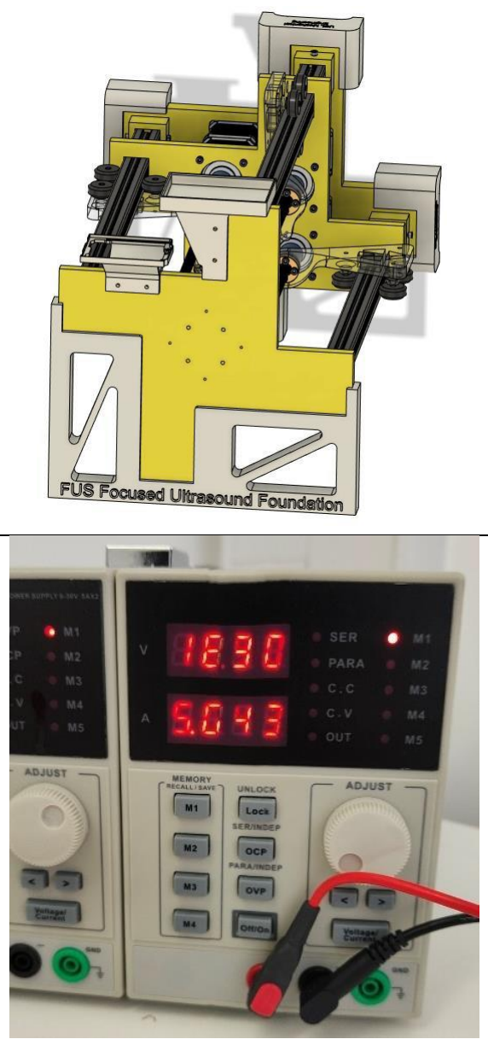
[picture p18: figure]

Table 4: Manufacture and assembly of driver module

### 4) Tendon Mechanism

From the last prototype, the tendon has been re-iterated to be fitted with compression springs instead of expansion springs. A backbone was also included so that the distance between each ligament was fixed and there would not be any shearing motion. It also acts as support to take the load off the springs improving the rigidity of the tendon. The backbone needs to be able to freely rotate around a pivot so an universal joint was chosen for this purpose.

4.1) CAD Model

Figure 56: CAD model for tendon

The tendon consists of eight ligaments spaced 50mm apart achieving a total length of 385mm. The diameter was 70mm to match that of the driver mechanism. Each ligament was connected with four 5mm inner diameter compression springs and an universal joint. A modular design was chosen for the purpose so that each section can be attached to the next with M3 bolts such that the length of the tendon can be easily adjusted to suit different purposes and needs. The base has four screws positioned to attach to the driving module whereas the subsequent joints only use two to save weight.

4.2) Manufacture And Assembly The ligaments were 3D printed on a Harlot
lite resin printer. The parts were then
removed and washed in a tub of isopropyl alcohol.

Using a generous amount of epoxy resin or Araldite, the springs were glued onto the ligaments and allowed to cure for four hours.

The universal joint was attached to the cured section and secured using an Allen hex key.

Each unit of the tendon was attached to the following section using M3 nuts and bolts and tightened using a hex key. This step was rather cumbersome and an M3 ratchet is highly recommended to ensure a secure fit.

4.3) Testing

Table 5: Manufacture and assembly of tendon

Initially, a test run was carried out with a four-section tendon. No end effector was installed to isolate the response under no load. The tendon was bolted to the driver base with four M3 nuts and bolts. A fishing line was then tied around the slider and passed through each section of the ligament before knotting at the end of the tendon. This was repeated for all four actuators using the same method. Finally, the slacks in the lines were removed through tensioning by rotating the threaded rod counterclockwise.

Figure 57: Line tensioning

The results showed the mechanism being functional and achieving manipulation in all directions. There was no sign of the tendon collapsing and all components remained intact.

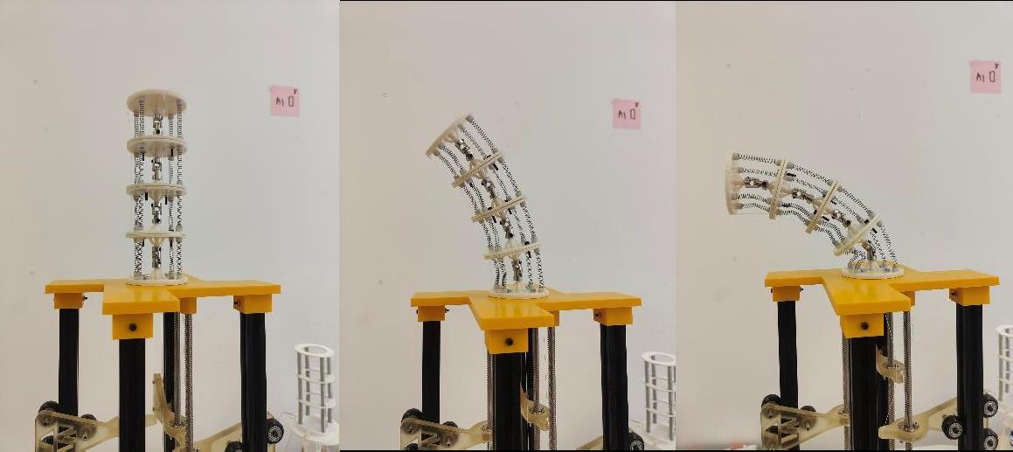
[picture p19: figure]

Figure 58,59,60: Manipulation of tendon with joystick

Upon a successful initial trial, four more sections were added to achieve the required workspace of 300mm. The same procedure was used to set up the test, reattaching and tensioning the fishing lines. However, the tendon was unable to support itself in the upright position and became very unstable failing at the second joint and undergoing collapse.

Figure 61,62,63: Tendon failure with eight sections

4.4) Prototype Evaluation
The initial test was promising in achieving successful actuation of the tendon using stepper motors and an user joystick input. It gave an insight into how the robot would perform and serves as a base for improvement. Stronger springs need to be used since the previous model was unable to support its weight even without the additional load of an ultrasonic transducer. Thus, the backbone strength and the rigidity of the tendon must be increased.
4.5) Design Improvements
To increase the rigidity of the tendon, the 5mm springs can be replaced with stiffer counterparts with a higher spring constant. In addition, reducing the distance between each ligament would increase the force needed to achieve the same displacement. As a result, the new design utilises much stronger, 8mm inner diameter springs with a length reduced to 35mm instead of 48mm. Furthermore, since the universal joints did not offer any resistance to bending, this was replaced with a die spring designed to handle higher loads. The spring was still able to bend in any direction whilst providing support to improve the strength and ability of the tendon to carry a higher load without collapse. The end effector should also be detachable as it was previously discovered that to change transducers, all the strings needed to be cut which would not be the case if a mount was made as the interphase between the tendon and the end effector. Furthermore, a standard housing for the breadboard was included so that a different adaptor can be used for a different-sized ultrasonic transducer whilst maintaining the existing sponsors and simply moving them to the new mount.

Figure 64: Die spring (left) and 8mm spring (right)

4.6) CAD Model

Figure 65: CAD model of improved tendon

The housing for the previous 5mm compression springs was modified to accommodate the larger springs. Furthermore, to prevent joint failure and causing the glued spring to dislocate under load, the wall height was increased from 5mm to 8mm. The mount for the central spring was also remodelled and updated. Finally, the number of bolts holding each joint together was increased from two to four to reduce the joints from deforming and coming apart under load. The detachable end effector was designed to be bolted onto the tendon using M3 bolts and holds the measuring instruments and transducer.

4.7) Manufacture And Assembly The construction follows an identical process to the previous tendon except with the new parts and Araldite was used to glue everything in place.

Figure 66: Comparison of old and new tendon design

Four M3 bolts were passed through the transducer mount as attachment points to the tendon. The transducer was then installed onto the mount and cover using M6 bolts after alignment in the correct orientation.

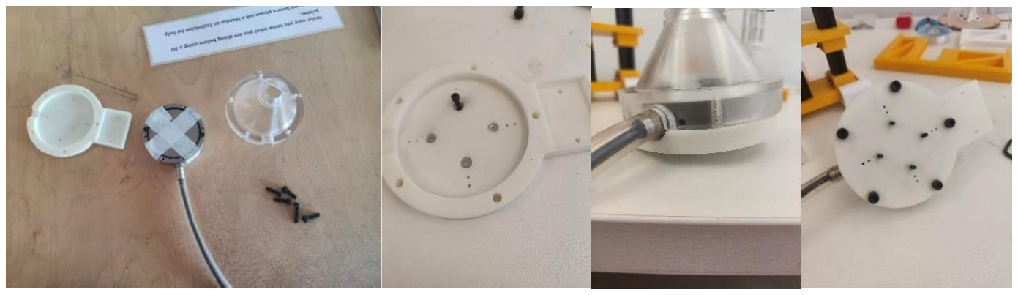
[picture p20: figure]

Figure 67,68,69,70: Ultrasonic transducer mount

Following this, the electronics breadboard was attached using two M3 bolts and the force transducer was fixed to the transducer cap with double-sided tape. The LCD and Arduino mounts were also 3D printed and fixed with M3 bolts. The tendon was attached to the base and strings tied and tensioned. Finally, the end effector was attached to the tendon using M3 nuts completing the prototype.

Figure 71,72,73: Completed robot

4.8) Testing
The prototype was tested in both the upright and the landscape orientation. Upon input via the joystick, the robot was successfully manipulated to bend and move the ultrasonic transducer in a semicircular region with the radius being the length from the base of the tendon to the tip of the transducer. All the instruments are accurate in measuring and displaying the orientation, distance to the subject and force exerted on the tip of the transducer.

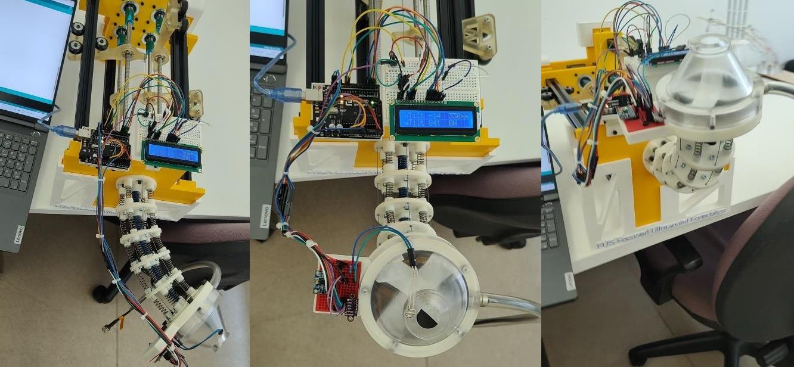
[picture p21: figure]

Figure 74,75,76: Manipulation of robot via joystick

The robot was tested to failure pushing on the joystick until the tendon bent back on itself. It was found that there were several weak points of the robot:

- Under intense load, the glue between the tendons and the springs were not strong enough and the springs popped out of their housing. This could be solved with a pin passing from the side of the mount through the spring securing it in place. These can then be reinforced with Araldite.

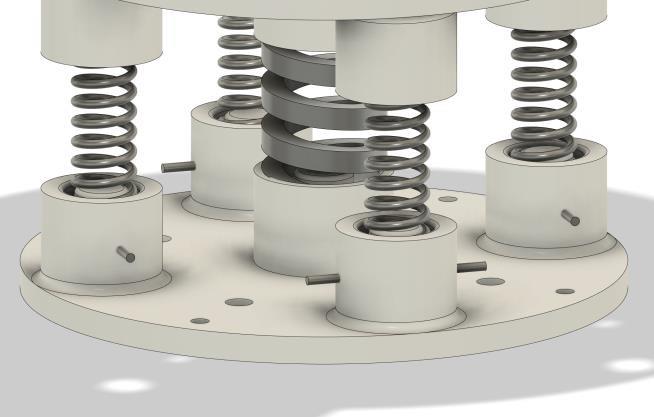
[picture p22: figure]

Figure 77: Design suggestion with pin inserts

- The top joint of the tendon was too weak snapping and breaking under intense load from the strings. This could be solved by increasing the thickness of the top joint.

Figure 78: Deforming ligaments and snapped joint

- The ligaments started deforming around the bolt curling up under load. This does not affect the performance of the robot but would become an issue over time causing fatigue in the part leading to eventual failure. This can be solved by adding more bolts around the circumference. However, a better solution would be to replace the 3D-printed ligaments with machined aluminium parts.
4.9) Prototype Evaluation
This prototype was the first time that the transducer and sensors were mounted and manipulated successfully. It showed very promising futures for the project with the robot being able to successfully manipulate the transducer while providing real-time information on the orientation, distance and force applied on the subject. It does have limitations and weaknesses including only being able to reach a fixed radius cone around the tendon and the glued joints failing under load which makes it too unreliable and unpredictable for the next stages of trials. Overall, the prototype was a solid basis for proving all the fundamental features of the tendon driving design but can be significantly improved in future iterations.

### 5) Cost Of Robot

All the components needed for the robot were broken down with purchase links in Appendix
4. The total cost of the robot comes out to be £332.58 which was below the 500-pound proposal. However, this does not include the costs for machinery and tools to build the robot which are sums to a further £388 with cost breakdowns in Appendix 5.

## IV – Conclusion

## A) Suggestions For Future Research

Future prototypes should aim to improve the capability and reliability of the robot whilst keeping existing features including the modular nature of the tendon and the ability to swap to different sensors without having to redesign the sensor circuit. The current design was mainly hardware-focused and more research should be focused on the simulation and coding aspect of the tendon. Simulations will help achieve a better understanding of the dynamic behaviour of the tendon and offer guidance with the selection of spring constants for different tendon lengths and weights of the ultrasonic transducer. This will make the design more calculated and less trial and error.

Currently, the design only has three rotational degrees of freedom but was not able to move linearly. Future designs should increase the degrees of freedom making the robot much more capable of reaching places within 3D space. To increase the degrees of freedom, the whole mechanism can be mounted onto a CNC gantry. This adds three more degrees of freedom allowing the robot to achieve 6 degrees of freedom and position itself anywhere within space.

Another solution could be to implement a tendon-locking system developed by the Diller micro-robotics lab at the University of Toronto. [35] The mechanism inhibits relative motion after the mechanism has been engaged.

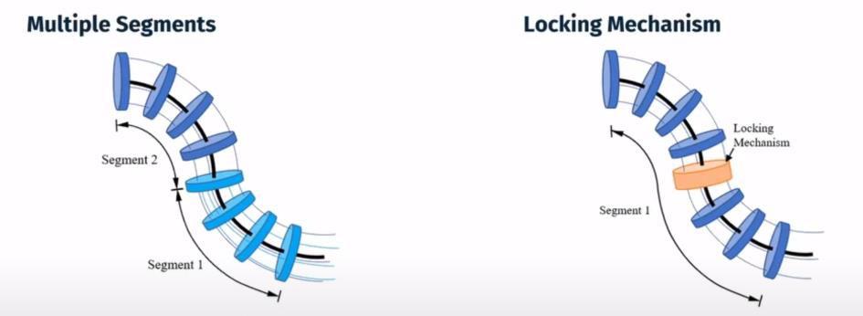
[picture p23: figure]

Figure 79: Locking mechanism

Initially, the entire tendon can be manipulated as one single segment. However, at any time, locking mechanisms can be used to clamp the strings and keep the latter section of the tendon fixed in place. From this point onwards, the initial section of the robot can be manipulated without changing the curvature of the second half. This can be repeated for numerous locking mechanisms. Thus, multiple degrees of freedom can be achieved without the need for additional segments. This not only eliminates the additional strings required for other segments but also maintains the number of driving stepper motors to the current four rather than having to add more driving units.

Figure 80: Incorporation of multiple locking mechanisms

The code for actuation can also be developed to become much more powerful including algorithms to automate the tendon and apply ultrasound along a pre-determined path. However, this would require further development from the mathematical dynamic modelling of the tendon.

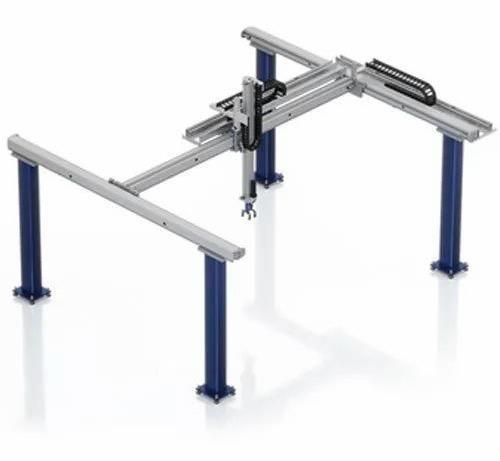
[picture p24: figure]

Figure 81: Cartesian gantry system [36]

Another potential field of research lies within the miniaturisation of tendon-driven robots. The tendons can be downscaled to fit micro high-intensity focused ultrasound transducers such as the Siansonic FUS transducer with a diameter of 4-6mm.

Figure 82: Micro transducers by Siansonic [37]

These micro tendons can then be fitted with endoscopes and perform in-vitro treatment from within the human body. The end effector can also easily be changed to other surgical tools such as a scalpel. Due to their small size, the surgeon would be able to insert and accurately guide the tendon within the human body to the target location.

## B) Summary

In conclusion, the solution to the inaccessibility of FUS manipulators has been met with a robotic manipulator. Thorough research was carried out to identify the optimal type of manipulator and extensive background research was completed on the topic. Following this, a simple prototype was made to assess the feasibility of the robot and provide useful feedback on its performance. Two more prototypes were made after this each with their iterations in improving parts of the design or trying out other potential options. Extensive testing was also carried out at each stage providing feedback to further improve the design. For the final prototype, a total of thirty-four iterations were carried out to achieve the current design.

Figure 83: Evolution of all three prototypes

There have been many challenges along the way including programming bugs and circuit wiring. Each iteration brought along discoveries and weaknesses within the design which were rectified and improved in the next iteration. However, in the end, the robot was successfully able to manipulate a FUS transducer using a joystick input. Distance, gyroscope and pressure sensors were also successfully integrated and relayed through an onboard LCD. The aim to keep the total cost under 500 pounds has also been met with all the materials and components required summing to 332.58 pounds.

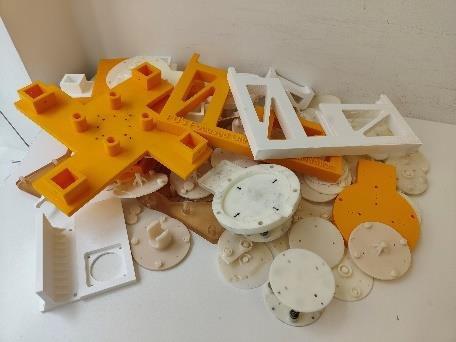
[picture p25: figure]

Figure 84: Failed and discarded 3D prints

I am thrilled by the progress and results achieved in this project, and the outcomes hold great promise for advancements in focused ultrasound research. I encourage fellow researchers to engage with the robot, explore its potential, and contribute to its ongoing development.

## V – References

[1] Claroline connect - Université Lyon1 (2023) Accueil. Available at: https://clarolineconnect.univ-lyon1.fr/ (Accessed: 20 July 2023).
[2] MGIUS-R3 robotic ultrasound system-MGI-leading life science innovation (2020) MGI. Available at: https://en.mgi-tech.com/products/instruments_info/11/ (Accessed: 20 July 2023).
[3] IOPscience (2021). Available at: https://iopscience.iop.org/ (Accessed: 20 July 2023).
[4] KR 4 agilus (2023) KUKA AG. Available at: https://www.kuka.com/enus/products/robotics-systems/industrial-robots/kr-4-agilus (Accessed: 20 July 2023).
[5] Joseph, L. (2020) Robot kinematics in a nutshell, Robotics. Available at: https://robocademy.com/2020/04/21/robot-kinematics-in-a-nutshell/ (Accessed: 23 July 2023).
[6] Parallel Robot (2019) Parallel Robot - an overview | ScienceDirect Topics. Available at:
https://www.sciencedirect.com/topics/computer-science/parallel-robot (Accessed: 23 July 2023).
[7] Build your own arduino-based Delta robot with Delta X (2019) Arduino Blog. Available at: https://blog.arduino.cc/2019/08/29/build-your-own-arduino-based-delta-robot-withdelta-x/ (Accessed: 23 July 2023).
[8] Hybrid control of robot manipulators (2022) | IEEE conference publication ... Available
at: https://ieeexplore.ieee.org/document/1087304/ (Accessed: 23 July 2023).
[9] Moser, B.L., Gordon, J.A. and Petruska, A.J. (2021) Unified Parameterization and calibration of serial, parallel, and hybrid manipulators, MDPI. Available at: https://www.mdpi.com/2218-6581/10/4/124 (Accessed: 23 July 2023).
[10] Explore scientific, technical, and medical research on ScienceDirect (2018)
ScienceDirect.com | Science, health and medical journals, full text articles and books.
Available at: https://www.sciencedirect.com/ (Accessed: 23 July 2023).
[11] Ender-3 pro 3D printer (2022) creality. Available at: https://www.creality.com/products/ender-3-pro-3d-printer (Accessed: 24 July 2023).
[12] Welcome to the Open CR Project (2020) opencontinuumrobotics.com. Available at: https://www.opencontinuumrobotics.com/ (Accessed: 24 July 2023).
[13] Considerations for follow-the-leader motion of extensible tendon-driven (2021) ... Available at: https://www.semanticscholar.org/paper/Considerations-for-follow-theleader-motion-of-Neumann-Burgner-Kahrs/775d5c003a3091de4a3fe1ec067d30a2a680c9cf (Accessed: 24 July 2023).

[14] Joints and links of robot | download scientific diagram (2021) - researchgate.
Available at: https://www.researchgate.net/figure/Joints-and-Links-of-Robot_fig4_301895257 (Accessed: 24 July 2023).
[15] Automated motion control of the Coast Robotic Guidewire (2019) ... - IEEE xplore. Available at: https://ieeexplore.ieee.org/abstract/document/9661508/ (Accessed: 28 July 2023).
[16] A continuum manipulator for open-source surgical robotics (2021) ... - IEEE XPLORE. Available at: https://ieeexplore.ieee.org/document/9273083 (Accessed: 28 July 2023).
[17] 440 piece M3 Bolts and nuts set, 304 Allen head screw bolts and nuts assortment kit, Allen machine screws with 2 pieces hex wrench (stainless steel)2023 (2023) Amazon.co.uk: DIY & Tools. Available at: https://www.amazon.co.uk/Stainless-Socket-Assortment-Machine-Wrenches/dp/B093GNHWKR (Accessed: 28 July 2023).
[18] Personal use download (2023) Autodesk. Available at: https://www.autodesk.com/products/fusion-360/personal-form-v2 (Accessed: 30 July 2023).
[19] Using the SG90 servo motor with an Arduino (2022) Electronics. Available at: https://www.electronics-lab.com/project/using-sg90-servo-motor-arduino/ (Accessed: 30 July 2023).
[20] Azdelivery 3 x GY-521 MPU-6050 3 Axis Gyroscope and Accelerometer 6DOF Sensor Module 16 bit AD converter data output IIC I2C compatible with Arduino and Raspberry Pi including e-book! (2023) Amazon.co.uk: Business, Industry & Science. Available at:
https://www.amazon.co.uk/gp/product/B07N2ZL34Z/ref=ppx_yo_dt_b_asin_title_o02_s00?ie=UTF8&th=1 (Accessed: 1 August 2023).
[21] MPU6050 interfacing with Arduino Uno: Arduino (2018) ElectronicWings. Available at: https://www.electronicwings.com/arduino/mpu6050-interfacing-with-arduino-uno (Accessed: 1 August 2023).
[22] Anon et al. (2022) Ultrasonic sensor HC-SR04 and Arduino - Complete Guide, How To Mechatronics. Available at: https://howtomechatronics.com/tutorials/arduino/ultrasonic-sensor-hc-sr04/(Accessed: 3 August 202323).
[23] Ravi, A.K. (2019) How to use ultrasonic sensor HC SR04 in Arduino, C# Corner. Available at: https://www.c-sharpcorner.com/UploadFile/167ad2/how-to-useultrasonic-sensor-hc-sr04-in-arduino/ (Accessed: 3 August 2023).
[24] Industries, A. (2023) Adafruit VL53L0X time of flight distance sensor - ~30 to 1000mm, adafruit industries blog RSS. Available at: https://www.adafruit.com/product/3317 (Accessed: 3 August 2023).

[25] Azdelivery VL53L0X time-of-flight GY-VL53L0XV2 long distance measurement sensor breakout 940nm GY-530 TOF laser range finder 2.8V 3.3V 5V I2C IIC compatible with Arduino including e-book! (2023) Amazon.co.uk: DIY & Tools. Available at:
https://www.amazon.co.uk/gp/product/B086V37JJ7/ref=ppx_yo_dt_b_asin_title_o08_s00?ie=UTF8&th=1 (Accessed: 5 August 2023).
[26] Sensore di Distanza GY-VL53L0XV2 VL53L0X time-of-flight distance sensor (2020) Makerslab Fablab. Available at: https://www.makerslab.it/sensore-di-
distanza-gy- (https://www.makerslab.it/sensore-di-distanza-gy-) | vl53l0xv2-vl53l0x-time-of-flight-distance-sensor/ | (Accessed: | 5
August 2023).
[27] Force sensor pressure, force sensing resistor 1 pc DF9-40 high precise resistance-type thin film pressure sensor force sensor for Arduino DIY kit(0-10kg) (2023) Amazon.co.uk: Business, Industry & Science. Available at: https://www.amazon.co.uk/gp/product/B07RJS2LVV/ref=ppx_yo_dt_b_asin_title_o09_s00?ie=UTF8&psc=1 (Accessed: 5 August 2023).
[28] Ada, Lady (2021) Force sensitive resistor (FSR), Adafruit Learning System. Available at: https://learn.adafruit.com/force-sensitive-resistor-fsr/using-an-fsr (Accessed:10 August 2023).
[29] Team, T.A. (2022) Liquid Crystal Displays (LCD) with Arduino, Arduino Documentation. Available at: https://docs.arduino.cc/learn/electronics/lcd-displays/(Accessed:10 August 2023).
[30] Iverntech 4pcs 600mm 2020 V type Black European standard anodized linear rail aluminum profile extrusion for DIY 3D printer and CNC Machine (2023) Amazon.co.uk: Business, Industry & Science. Available at: https://www.amazon.co.uk/gp/product/B087PVGPRF/ref=ppx_yo_dt_b_asin_title_o05_s00?ie=UTF8&th=1 (Accessed:10 August 2023).
[31] TB6600_Stepper_Motor_Driver_SKU DRI0043 (2021) DFRobot. Available at: https://wiki.dfrobot.com/TB6600_Stepper_Motor_Driver_SKU DRI0043 (Accessed:10 August 2023).
[32] Covvy TB6600 4A DC 9-42V Stepper Motor Driver CNC Controller 32 segments 2/4 Phase Hybrid Stepper Motor Driver Board (2023) Amazon.co.uk: Business, Industry & Science. Available at:
https://www.amazon.co.uk/gp/product/B07SBZ9SM5/ref=ppx_yo_dt_b_asin_title_o02_s00?ie=UTF8&psc=1 (Accessed:10 August 2023).
[33] Pulse width modulation (2022)- basic electronics tutorials and Revision. Available at: https://www.electronics-tutorials.ws/blog/pulse-width-modulation.html (Accessed:12 August 2023).
[34] Ali, A. (2023) Joystick controlled mouse with Arduino, Circuits DIY. Available at: https://www.circuits-diy.com/joystick-controlled-mouse-with-arduino/ (Accessed:15 August 2023).

[35] chair, E. (2023) E-media chair, IROS 2022. Available at https://iros2022.org/(Accessed: 3 September 2023).
[36] 3 Axis Gantry Linear Robot (2023) indiamart.com. Available at: https://www.indiamart.com/proddetail/3-axis-gantry-linear-robot-22561824888.html (Accessed: 3 September 2023).
[37] Ultrasonic transducers: Siansonic technology (2023) Siansonic. Available at: https://www.siansonic.com/Products/Ultrasonic-Transducer (Accessed: 5 September 2023).

## VI – Appendix

## Appendix.1

#include <Servo.h>

Servo myservo; // create servo object to control a servo

int potpin = 0;

int val;

void setup() {

myservo.attach(9);

}

void loop() {

val = analogRead(potpin);

val = map(val, 0, 1023, 0, 180);

myservo.write(val);

delay(15);

}

## Appendix.2

#include <Stepper.h>

int Xspeed;

int Xspeedmap1;

int Xspeedmap2;

int Yspeed;

int Yspeedmap1;

int Yspeedmap2;

const int stepX=2;

const int dirX=3;

const int stepY=4;

const int dirY=5;

const int stepZ=6;

const int dirZ=7;

const int stepA=12;

const int dirA=13;

void setup() {

pinMode(stepX,OUTPUT);

pinMode(dirX,OUTPUT);

pinMode(stepY,OUTPUT);

pinMode(dirY,OUTPUT);

p3

-inMode(stepZ,OUTPUT);

pinMode(dirZ,OUTPUT);

pinMode(stepA,OUTPUT);

pinMode(dirA,OUTPUT);

Serial.begin(9600);

}

void loop()

{

Xspeed=analogRead(A0);

Xspeedmap1=map(Xspeed,0,1023,100,4000);

Xspeedmap2=map(Xspeed,0,1023,4000,100);

Yspeed=analogRead(A1);

Yspeedmap1=map(Yspeed,0,1023,40,4000);

Yspeedmap2=map(Yspeed,0,1023,4000,40);

if (Xspeed<510){

digitalWrite(dirX,LOW);

digitalWrite(stepX,LOW);

digitalWrite(stepX,HIGH);

digitalWrite(dirY,HIGH);

digitalWrite(stepY,LOW);

digitalWrite(stepY,HIGH);

delayMicroseconds(Xspeedmap1);

}

if (Xspeed>530){

digitalWrite(dirX,HIGH);

digitalWrite(stepX,LOW);

digitalWrite(stepX,HIGH);

digitalWrite(dirY,LOW);

digitalWrite(stepY,LOW);

digitalWrite(stepY,HIGH);

delayMicroseconds(Xspeedmap2);

}

if (Yspeed<510){

digitalWrite(dirZ,LOW);

digitalWrite(stepZ,LOW);

digitalWrite(stepZ,HIGH);

digitalWrite(dirA,HIGH);

digitalWrite(stepA,LOW);

digitalWrite(stepA,HIGH);

delayMicroseconds(Yspeedmap1);

}

if (Yspeed>530){

digitalWrite(dirZ,HIGH);

digitalWrite(stepZ,LOW);

digitalWrite(stepZ,HIGH);

digitalWrite(dirA,LOW);

digitalWrite(stepA,LOW);

digitalWrite(stepA,HIGH);

delayMicroseconds(Yspeedmap2);

}

}

## Appendix.3

#include "Wire.h"

#include "I2Cdev.h"

#include "MPU6050.h"

#include <Wire.h>

#include <VL53L0X.h>

#include <LiquidCrystal.h>

const int rs = 12, en = 11, d4 = 5, d5 = 4, d6 = 3, d7 = 2;

LiquidCrystal lcd(rs, en, d4, d5, d6, d7);

VL53L0X sensor;

int fsrPin = 0; | // the FSR and 10K pulldown are connected to a0
int fsrReading; | // the analog reading from the FSR resistor divider
int fsrVoltage; | // the analog reading converted to voltage

unsigned long fsrResistance; // The voltage converted to resistance, can be very big so make "long"

unsigned long fsrConductance;

long fsrForce; // Finally, the resistance converted to force

MPU6050 mpu;

int16_t ax, ay, az;
int16_t gx, gy, gz;

struct MyData {

int X;

int Y;

int Z;

};

MyData data;

void setup()

{

pinMode(12,INPUT_PULLUP);

digitalWrite(12,HIGH);

Serial.begin(9600);

Wire.begin();

lcd.begin(16, 2);

sensor.init();

sensor.setTimeout(500);

// Start continuous back-to-back mode (take readings as

// fast as possible). To use continuous timed mode

// instead, provide a desired inter-measurement period in

// ms(e.g.sensor.startContinuous(100)).

sensor.startContinuous();

Serial.begin(9600);

Wire.begin();

mpu.initialize();

//pinMode(LED_BUILTIN, OUTPUT);

}
void loop()

{

fsrReading = analogRead(fsrPin);

// analog voltage reading ranges from about 0 to 1023 which maps to 0V to 5V (= 5000mV)

fsrVoltage = map(fsrReading, 0, 1023, 0, 5000);

if (fsrVoltage == 0) {

Serial.println("No pressure");

} else {

// The voltage = Vcc * R / (R + FSR) where R = 10K and Vcc = 5V

// so FSR = ((Vcc - V) * R) / V | yay math!
fsrResistance = 5000 - fsrVoltage; | // fsrVoltage was in millivolts so 5V = 5000mV

fsrResistance *= 10000; | // 10K resistor

fsrResistance /= fsrVoltage;

fsrConductance = 1000000; // we measure in micromhos so

fsrConductance /= fsrResistance;

// Use the two FSR guide graphs to approximate the force

if (fsrConductance <= 1000) {

fsrForce = fsrConductance / 80;

Serial.print("Force in Newtons: ");

Serial.println(fsrForce);

} else {

fsrForce = fsrConductance - 1000;

fsrForce /= 30;

Serial.print("Force in Newtons: ");

Serial.println(fsrForce);

}

}
Serial.println(" --------------------");

delay(1000);

int distance =sensor.readRangeContinuousMillimeters();

//int distance =sensor.startContinuous(100);

distance = distance-64;

Serial.print("Distance: ");

Serial.print(distance);

Serial.print("mm");

if (sensor.timeoutOccurred()) { Serial.print(" TIMEOUT"); }

Serial.println();

mpu.getMotion6(&ax, &ay, &az, &gx, &gy, &gz);

data.X = map(ax, -17000, 17000, 0, 255 )-140; // X axis data

data.Y = map(ay, -17000, 17000, 0, 255)-2;

data.Z = map(az, -17000, 17000, 0, 255); // Y axis data

Serial.print("X-Tilt = ");

Serial.print(data.X);

Serial.print(" ");

Serial.print("Y-Tilt = ");

Serial.print(data.Y);

Serial.print(" ");

Serial.print(" ");

Serial.println();

lcd.setCursor(0, 0);

lcd.print("xTilt ");

lcd.print(data.X);

lcd.setCursor(11, 0);

lcd.print(distance);

lcd.print("mm");

lcd.setCursor(0, 1);

lcd.print("yTilt ");

lcd.print(data.Y);

lcd.setCursor(11, 1);

lcd.print(fsrForce);

lcd.print("N");

}

## Appendix.4

Component | Quantity | Quantity per pack | Cost (£) | Total cost (£) | Link for purchase
M3 nuts and bolts set | 1 | As needed | 8.39 | 8.39 | https://www.amazon.co.uk/Assortme nt-Stainless-Replacement-Machine-Fastener/dp/B0B3MGZ7T2/ref=sr_1 _4?crid=TKKTFT6H22UU&keywor ds=m3%2Bbolts&qid=1694550983 &s=industrial&sprefix=m3%2Bbolt %2Cindustrial%2C75&sr=1-4&th=1 (https://www.amazon.co.uk/Assortment-Stainless-Replacement-Machine-Fastener/dp/B0B3MGZ7T2/ref%3Dsr_1_4?s=industrial)
Stepper motor | 4 | 1 | 6.99 | 27.96 | https://item.taobao.com/item.htm?spm=a21n57.1.0.0.37a0523cbAI6ZF&id=567501925505&ns=1&abbucket=14#detail (https://item.taobao.com/item.htm?id=567501925505&ns=1&abbucket=14&detail%20)
Harmonic reducer | 4 | 1 | 5.45 | 21.8 | https://item.taobao.com/item.htm?spm=a21n57.1.0.0.37a0523cbAI6ZF&id=559484971599&ns=1&abbucket=14#detail (https://item.taobao.com/item.htm?id=559484971599&ns=1&abbucket=14&detail%20)
Stepper motor driver | 4 | 1 | 8.99 | 35.96 | https://www.amazon.co.uk/gp/product/B07SBZ9SM5/ref=ppx_yo_dt_b_asin_title_o06_s00?ie=UTF8&psc=1 (https://www.amazon.co.uk/gp/product/B07SBZ9SM5/ref%3Dppx_yo_dt_b_asin_title_o06_s00?ie=UTF8&psc=1)
100lb braided fishing line | 1 | 1 | 8.69 | 8.69 | https://www.amazon.co.uk/gp/product/B076FM9GKN/ref=ppx_yo_dt_b_asin_title_o02_s00?ie=UTF8&th=1&psc=1 (https://www.amazon.co.uk/gp/product/B076FM9GKN/ref%3Dppx_yo_dt_b_asin_title_o02_s00)
Compressio n springs | 20 | 10 | 6.49 | 12.98 | https://www.amazon.co.uk/gp/product/B08X6PZWT7/ref=ppx_yo_dt_b_asin_title_o03_s00?ie=UTF8&th=1 (https://www.amazon.co.uk/gp/product/B08X6PZWT7/ref%3Dppx_yo_dt_b_asin_title_o03_s00?ie=UTF8&th=1)
Die springs | 5 | 2 | 4.99 | 14.97 | https://www.amazon.co.uk/gp/product/B07LBTMGGR/ref=ppx_yo_dt_b_asin_title_o05_s00?ie=UTF8&th=1 (https://www.amazon.co.uk/gp/product/B07LBTMGGR/ref%3Dppx_yo_dt_b_asin_title_o05_s00?ie=UTF8&th=1)
Ball bearings | 4 | 4 | 7.49 | 7.49 | https://www.amazon.co.uk/gp/product/B07FXX4K4K/ref=ppx_yo_dt_b_asin_title_o07_s00?ie=UTF8&th=1 (https://www.amazon.co.uk/gp/product/B07FXX4K4K/ref%3Dppx_yo_dt_b_asin_title_o07_s00?ie=UTF8&th=1)
Slider wheels | 12 | 10 | 8.99 | 17.98 | https://www.amazon.co.uk/gp/product/B07SJ3VZ68/ref=ppx_yo_dt_b_asin_title_o05_s01?ie=UTF8&psc=1 (https://www.amazon.co.uk/gp/product/B07SJ3VZ68/ref%3Dppx_yo_dt_b_asin_title_o05_s01?ie=UTF8&psc=1)
Threaded screw | 4 | 2 | 6.99 | 11.98 | https://www.amazon.co.uk/gp/product/B093SHGY87/ref=ppx_yo_dt_b_asin_title_o04_s00?ie=UTF8&psc=1 (https://www.amazon.co.uk/gp/product/B093SHGY87/ref%3Dppx_yo_dt_b_asin_title_o04_s00?ie=UTF8&psc=1)
2020 Aluminium extrusion (600mm) | 4 | 4 | 28.99 | 28.99 | https://www.amazon.co.uk/gp/product/B087PVGPRF/ref=ppx_yo_dt_b_asin_title_o05_s00?ie=UTF8&th=1 (https://www.amazon.co.uk/gp/product/B087PVGPRF/ref%3Dppx_yo_dt_b_asin_title_o05_s00?ie=UTF8&th=1)
8mm to 10mm adaptor coupling | 4 | 2 | 6.99 | 13.98 | https://www.amazon.co.uk/gp/product/B07P967QQ8/ref=ppx_yo_dt_b_asin_title_o08_s00?ie=UTF8&th=1 (https://www.amazon.co.uk/gp/product/B07P967QQ8/ref%3Dppx_yo_dt_b_asin_title_o08_s00?ie=UTF8&th=1)

Arduino Uno starter kit | 1 | 1 | 36.54 | 36.54 | https://www.amazon.co.uk/gp/product/B01D8KOZF4/ref=ppx_od_dt_b_asin_title_s00?ie=UTF8&psc=1 (https://www.amazon.co.uk/gp/product/B01D8KOZF4/ref%3Dppx_od_dt_b_asin_title_s00?ie=UTF8&psc=1)
Arduino jumper cables | 1 | As needed | 8.99 | 8.99 | https://www.amazon.co.uk/gp/product/B0BRM568FM/ref=ppx_yo_dt_b_asin_title_o06_s00?ie=UTF8&th=1 (https://www.amazon.co.uk/gp/product/B0BRM568FM/ref%3Dppx_yo_dt_b_asin_title_o06_s00?ie=UTF8&th=1)
Gyroscope | 1 | 1 | 4.49 | 4.49 | https://www.amazon.co.uk/gp/product/B07N2ZL34Z/ref=ppx_yo_dt_b_asin_title_o02_s00?ie=UTF8&psc=1 (https://www.amazon.co.uk/gp/product/B07N2ZL34Z/ref%3Dppx_yo_dt_b_asin_title_o02_s00?ie=UTF8&psc=1)
Distance sensor | 1 | 1 | 6.49 | 6.49 | https://www.amazon.co.uk/gp/product/B086V37JJ7/ref=ppx_yo_dt_b_asin_title_o00_s00?ie=UTF8&th=1 (https://www.amazon.co.uk/gp/product/B086V37JJ7/ref%3Dppx_yo_dt_b_asin_title_o00_s00?ie=UTF8&th=1)
Force sensor | 1 | 1 | 4.63 | 4.63 | https://www.amazon.co.uk/gp/product/B07RJS2LVV/ref=ppx_yo_dt_b_asin_title_o09_s00?ie=UTF8&psc=1 (https://www.amazon.co.uk/gp/product/B07RJS2LVV/ref%3Dppx_yo_dt_b_asin_title_o09_s00?ie=UTF8&psc=1)
1kg PLA plastic filament | 2 | 1 | 19.54 | 39.08 | https://www.amazon.co.uk/Creality-High-Speed-Resistant-Performance-Dimensional/dp/B0C342YMWQ/ref=sr_1_2_sspa?crid=53M391QI9HQR&keywords=pla+filament&qid=1694550257&sprefix=pla+filament%2Caps%2C95&sr=8-2-spons&sp_csd=d2lkZ2V0TmFtZT1zcF9hdGY&psc=1 (https://www.amazon.co.uk/Creality-High-Speed-Resistant-Performance-Dimensional/dp/B0C342YMWQ/ref%3Dsr_1_2_sspa?sp_csd=d2lkZ2V0TmFtZT1zcF9hdGY)
1kg resin printer refill | 1 | 1 | 21.19 | 21.19 | https://www.amazon.co.uk/gp/product/B09XB3SLC7/ref=ppx_yo_dt_b_asin_title_o06_s00?ie=UTF8&psc=1 (https://www.amazon.co.uk/gp/product/B09XB3SLC7/ref%3Dppx_yo_dt_b_asin_title_o06_s00?ie=UTF8&psc=1)
| | | | | Total sum = £332.58

Table 6: Cost and purchase links for robot components

## Appendix.5

Component | Cost (£) | Link for purchase
Creality Ender v3 | 165 | https://www.amazon.co.uk/Comgrow-Creality-Ender-Printer-Aluminum/dp/B07BR3F9N6/ref=sr_1_1_sspa?crid=37H4RP2433KVZ&keywords=ender+3&qid=1694553869&sprefix=ender+%2Caps%2C109&sr=8-1-spons&ufe=app_do%3Aamzn1.fos.42a483c5-1df2-46ee-a728-92d018483bf9&sp_csd=d2lkZ2V0TmFtZT1zcF9hdGY&psc=1 (https://www.amazon.co.uk/Comgrow-Creality-Ender-Printer-Aluminum/dp/B07BR3F9N6/ref%3Dsr_1_1_sspa?sp_csd=d2lkZ2V0TmFtZT1zcF9hdGY)
Creality Harlot Lite | 149 | https://www.amazon.co.uk/Creality-Halot-Mage-Photocuring-High-Precision-8-97x5-03x9-05in-Halot-Mage/dp/B0BQJBVJLC/ref=sr_1_2?crid=3GZHCTD700F42&keywords=harlot%2Blite&qid=1694554065&sprefix=harlot%2Blit%2Caps%2C81&sr=8- (https://www.amazon.co.uk/Creality-Halot-Mage-Photocuring-High-Precision-8-97x5-03x9-05in-Halot-Mage/dp/B0BQJBVJLC/ref%3Dsr_1_2)
Cordless drill | 32.99 | https://www.amazon.co.uk/Terratek%C2%AE-Cordless-Lithium-Ion-Screwdriver-Accessory/dp/B00I506718/ref=sr_1_6?crid=5KLQN3C0F7BT&keywords=cordless+drill&qid=1694554128&sprefix=cordless+drill%2Caps%2C87&sr=8-6 (https://www.amazon.co.uk/Terratek%C2%AE-Cordless-Lithium-Ion-Screwdriver-Accessory/dp/B00I506718/ref%3Dsr_1_6)
Hex key set | 3.45 | https://www.amazon.co.uk/Rolson-Hex-Key-Set-1-5-10/dp/B001F66HHI/ref=sr_1_7?crid=3IZL2H9GDZRY3&keywords=allen%2Bkey&qid=1694554208&sprefix=allen%2Bkey%2Caps%2C89&sr=8-7&th=1 (https://www.amazon.co.uk/Rolson-Hex-Key-Set-1-5-10/dp/B001F66HHI/ref%3Dsr_1_7)
Soldering iron kit | 15.28 | https://www.amazon.co.uk/Soldering-Adjustable-Temperature-180-520%C2%B0C-Desoldering/dp/B092VTGGDM/ref=sr_1_5?crid=2SE69E2HYPR85&keywords=soldering+iron+kit&qid=1695925691&sprefix=soldering+iro%2Caps%2C91&sr=8-5 (https://www.amazon.co.uk/Soldering-Adjustable-Temperature-180-520%C2%B0C-Desoldering/dp/B092VTGGDM/ref%3Dsr_1_5)
Metal hacksaw | 15.99 | https://www.amazon.co.uk/AIRAJ-High-Tension-Replaceable-Comfortable-Woodworking/dp/B083BDHQYK/ref=sr_1_1_sspa?crid=1OEJYQDX1LKF8&keywords=metal%2Bhacksaw&qid=1695997243
| | &sprefix=metal%2Bhacksaw%2Caps%2C68&sr=8-1-spons&sp_csd=d2lkZ2V0TmFtZT1zcF9hdGY&th=1 (https://www.amazon.co.uk/AIRAJ-High-Tension-Replaceable-Comfortable-Woodworking/dp/B083BDHQYK/ref%3Dsr_1_1_sspa?sp_csd=d2lkZ2V0TmFtZT1zcF9hdGY)
Araldite | 6.29 | https://www.amazon.co.uk/Araldite%C2%AE-Standard-24ml-Syringe-Epoxy/dp/B006JYPUSI/ref=sr_1_1_sspa?crid=CH02OTKDZW95&keywords=araldite&qid=1694554162&sprefix=arayl%2Caps%2C75&sr=8-1-spons&sp_csd=d2lkZ2V0TmFtZT1zcF9hdGY&psc=1 (https://www.amazon.co.uk/Araldite%C2%AE-Standard-24ml-Syringe-Epoxy/dp/B006JYPUSI/ref%3Dsr_1_1_sspa?sp_csd=d2lkZ2V0TmFtZT1zcF9hdGY)

Table 7: Cost and purchase links for tools and machinery

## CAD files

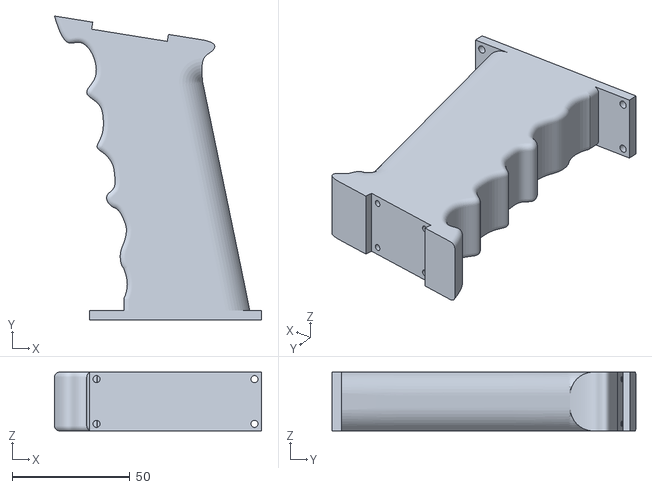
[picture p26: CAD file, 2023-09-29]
Robot CAD Files/Joystick Mount.stl
87.9 x 129.0 x 25.0

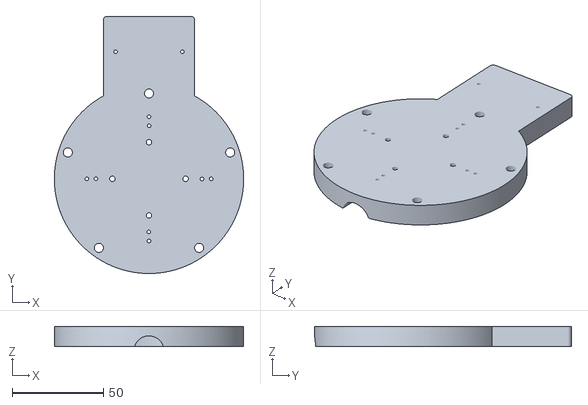
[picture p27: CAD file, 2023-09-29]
Robot CAD Files/Ultrasonic Transducer Mount.stl
103.5 x 140.5 x 11.0

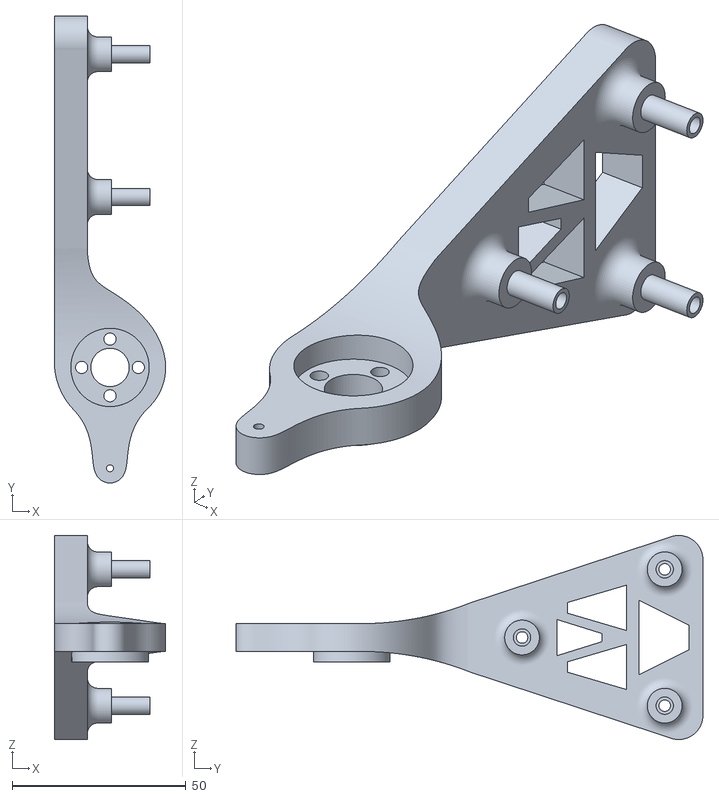
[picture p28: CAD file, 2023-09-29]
Robot CAD Files/Slider.stl
32.0 x 134.2 x 58.6

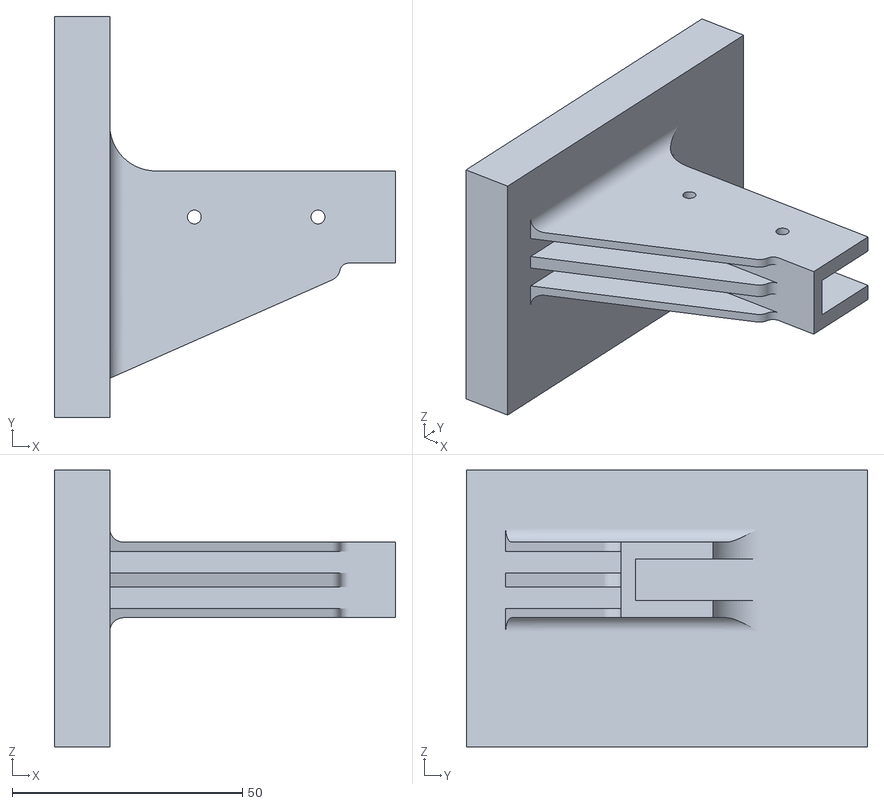
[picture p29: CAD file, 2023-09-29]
Robot CAD Files/LCD Mount.stl
74.0 x 87.0 x 60.0

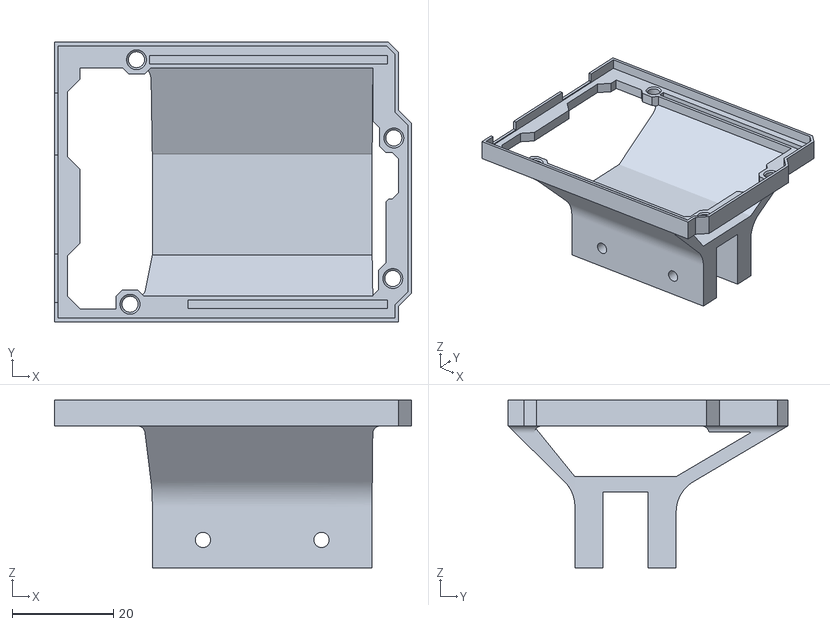
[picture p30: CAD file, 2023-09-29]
Robot CAD Files/Arduino Mount.stl
70.5 x 55.2 x 33.1

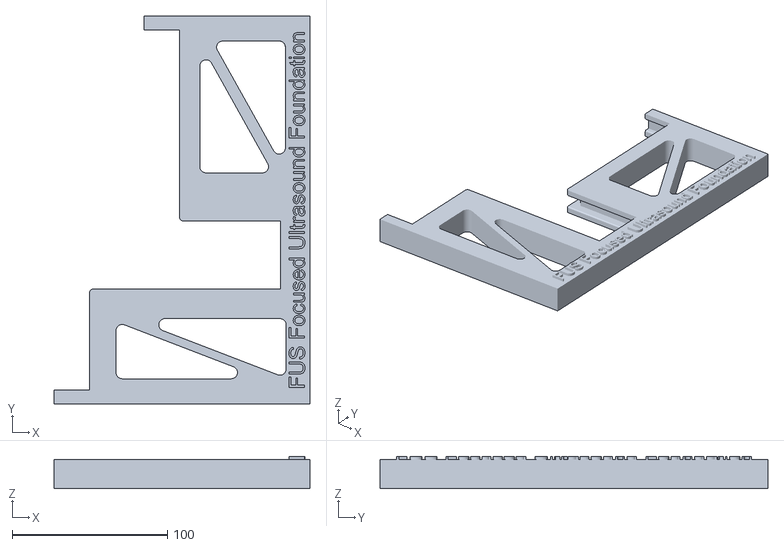
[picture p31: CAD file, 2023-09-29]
Robot CAD Files/Sideways Support Mount.stl
165.0 x 250.0 x 20.8

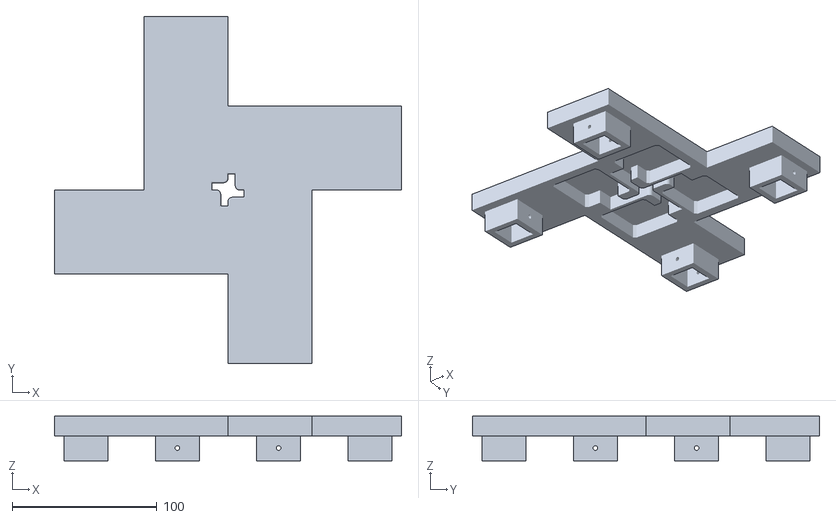
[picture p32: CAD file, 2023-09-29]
Robot CAD Files/Base Mount.stl
240.0 x 240.0 x 30.8

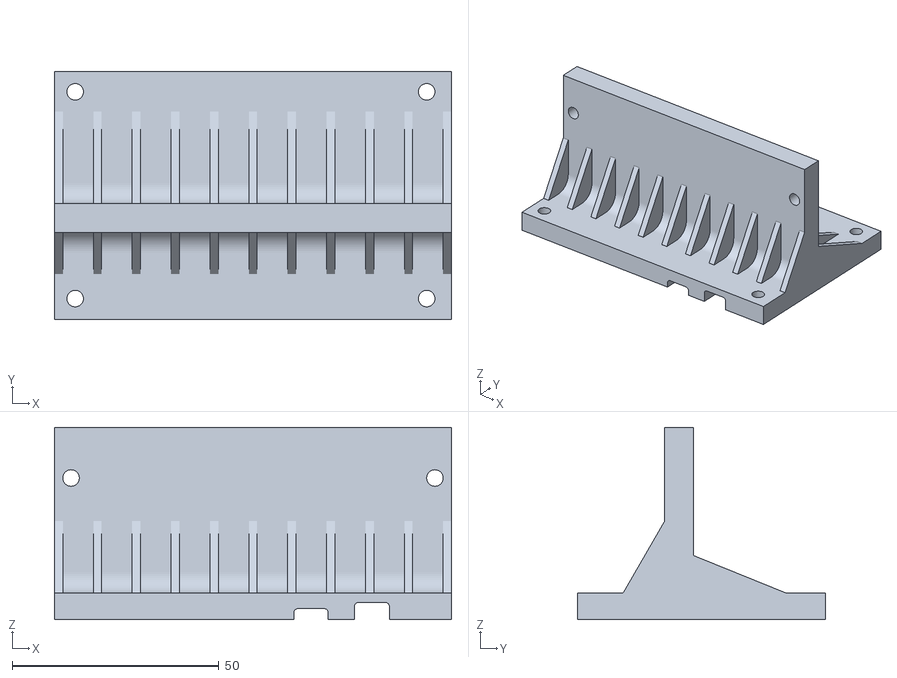
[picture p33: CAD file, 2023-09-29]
Robot CAD Files/Stepper Motor TB6600 Controller Mount.stl
96.0 x 59.9 x 46.5

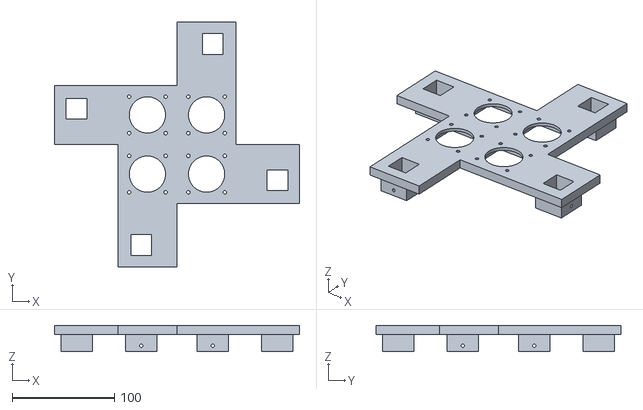
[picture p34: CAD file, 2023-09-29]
Robot CAD Files/Stepper Motor Mount.stl
240.0 x 240.0 x 25.8

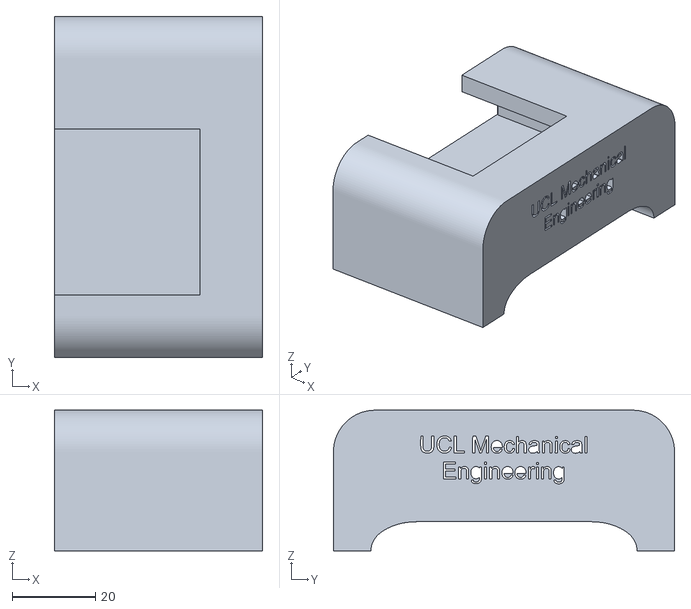
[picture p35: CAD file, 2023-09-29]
Robot CAD Files/Base Support Legs.stl
50.0 x 82.0 x 33.8

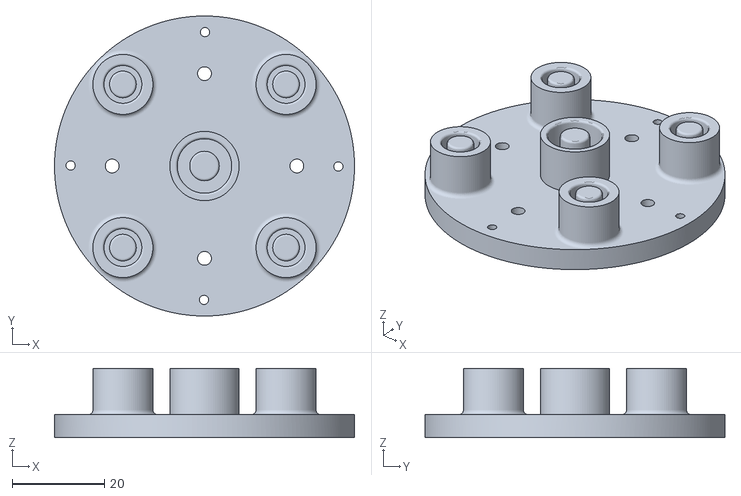
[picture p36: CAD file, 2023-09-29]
Robot CAD Files/Tendon Ligaments.stl
65.0 x 65.0 x 15.0

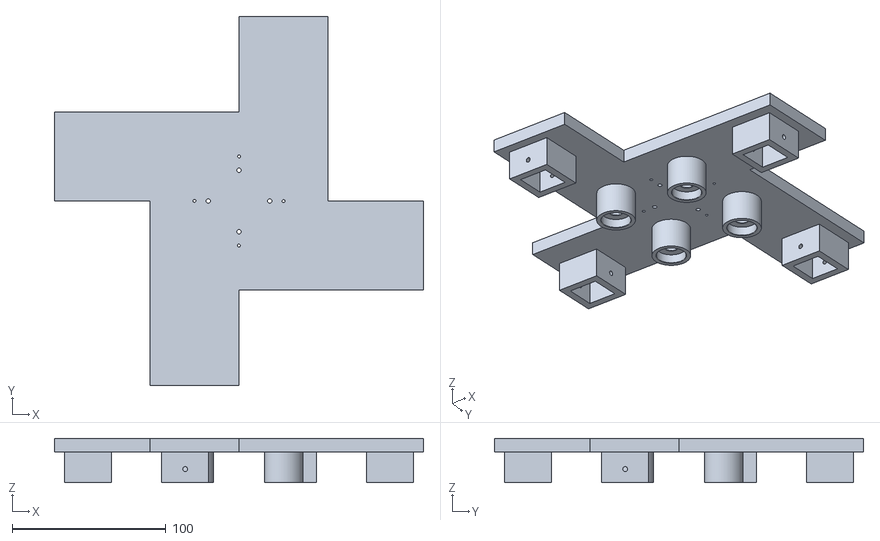
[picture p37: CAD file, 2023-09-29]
Robot CAD Files/Top Mount.stl
240.0 x 240.0 x 28.8
